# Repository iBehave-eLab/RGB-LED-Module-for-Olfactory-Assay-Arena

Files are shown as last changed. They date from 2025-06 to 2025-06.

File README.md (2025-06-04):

# RGB-LED-Module-for-Olfactory-Assay-Arena

The RGB LED Module "Model 608 revC V1.0" is specifically designed for use with the "Olfactory Assay Arena" Revision C and enables precise optogenetic control in behavioral experiments. The board supports independent control of red, green, and blue high-power LEDs across four separate channels, as well as an independently controlled IR LED. It interfaces with an Arduino Mega 2560 via serial communication, using PWM and TTL signals for intensity and status regulation. Safety features and operational constraints ensure reliable use in a laboratory setting. A comprehensive command structure allows for highly flexible integration into custom research setups. This system is not approved for human use and is intended strictly for experimental laboratory environments.

 ### Pictures

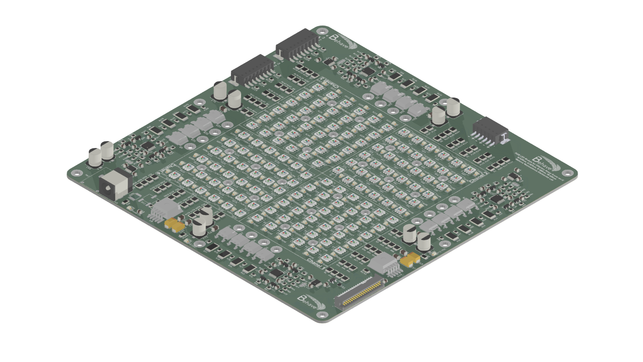
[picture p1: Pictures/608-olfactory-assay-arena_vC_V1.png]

_Rendering of the RGB-LED-Module-for-Olfactory-Assay-Arena (by Mehrdad Ghanbari)._

## Reference
The RGB-LED module "Model 608 revC V1.0" was designed as a drop-in replacement for the original single-color LED module used in the “Olfactory Assay Arena – Revision C” developed by HHMI’s Janelia Research Campus.

https://www.janelia.org/open-science/four-way-olfactometer-arena-fruit-flies
https://hhmi.flintbox.com/technologies/c65b2ddd-3cc1-44d9-a95d-73e08723f724

Our contribution is limited to adapting the original PCB layout to support three-color RGB LEDs. All mechanical components and the intended use case remain unchanged and originate entirely from the original design provided by the Janelia Research Campus.

This repository is intended solely for research and prototyping purposes. All rights to the original design and its application belong to HHMI’s Janelia Research Campus.

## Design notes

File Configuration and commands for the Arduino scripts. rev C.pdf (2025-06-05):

# RGB LED Module for Olfactory Assay Arena rev:C Model 608 revC V1.0

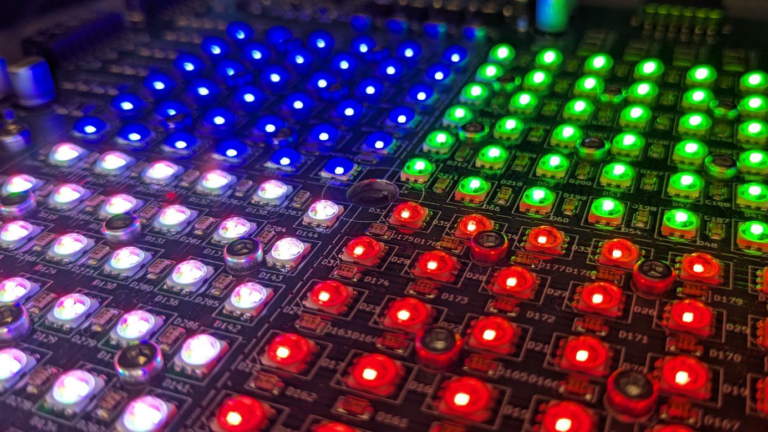
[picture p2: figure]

# OPERATOR’S MANUAL

Version A
May 2025

608 rev C V 1.0 Operator's Manual

This manual refers to the RGB LED Module for the Olfactory Assay Arena, Revision C, as currently provided (as of April 2025, version 608-C-1) by the Neuroscience Electronics Lab at the Institute of Zoology, University of Cologne.
Contacts:
- mehrdad.ghanbari@uni-koeln.de (Mehrdad Ghanbari)

The following commands are intended for use with a serial terminal. It is important to ensure that the interface baud rate is set to 115200 bits per second.
This version of the optogenetic arena uses RGB LEDs. Therefore, it is necessary to adapt the corresponding Arduino scripts to enable precise control of the LEDs. This includes modifications to the Arduino commands and configurations, as well as appropriate adjustments in serial terminal communication tools.
Important Information • The Model 608 revC V1.0 and its associated parts are not intended for experiments on

humans and must not be used for that purpose.Use on humans is strictly prohibited, unless specifically marked and insulated probes designed for such applications are used.This device is intended for laboratory use only.
- Before powering up the board, please ensure that the TTL/PWM Interface Board is properly connected to the RGB LED Module for the Olfactory Assay Arena, Revision C using the appropriate cables.This prevents the RGB LEDs from turning on unexpectedly without a command or signal.
- Do not touch the boards while they are powered on and under voltage.
- This may cause damage to components or lead to unintended malfunction. Maximum Brightness and Power Distribution The total intensity per channel must not exceed 100 %. This means:
1. You can run one LED color at 100 % while the others are off,
2. or two colors at 50 % each,
3. or three colors at approximately 35 % each.
If all three colors (Red, Green, Blue) are operated at full brightness simultaneously (3 × 100 % = 300 % on one channel), the remaining three channels must not exceed a combined total of 100 % brightness.
Thus, the total output across all four channels must not exceed 400 %.
The IR LED operates independently from the RGB LEDs and can be freely set between 0 and 100 % brightness without affecting this limitation.

# Installationshinweis

Installing the Model 608 revC V1.0 in a laboratory setting is very straightforward. It can be operated on almost any standard lab bench.
The “RGB LED Module for the Olfactory Assay Arena, Revision C” board features two power input jacks:
- Ø 2.5 mm (inner) for 24 VDC / 5 A
- Ø 2.1 mm (inner) for 9 VDC / 0.6 A

The appropriate power supplies are included.
The Arduino is powered using the included 9 VDC power supply.

Make sure the power supply matches the voltage requirements of the connected boards before plugging it in.
Do not block the ventilation side of the board to prevent overheating.

# Block Diagra

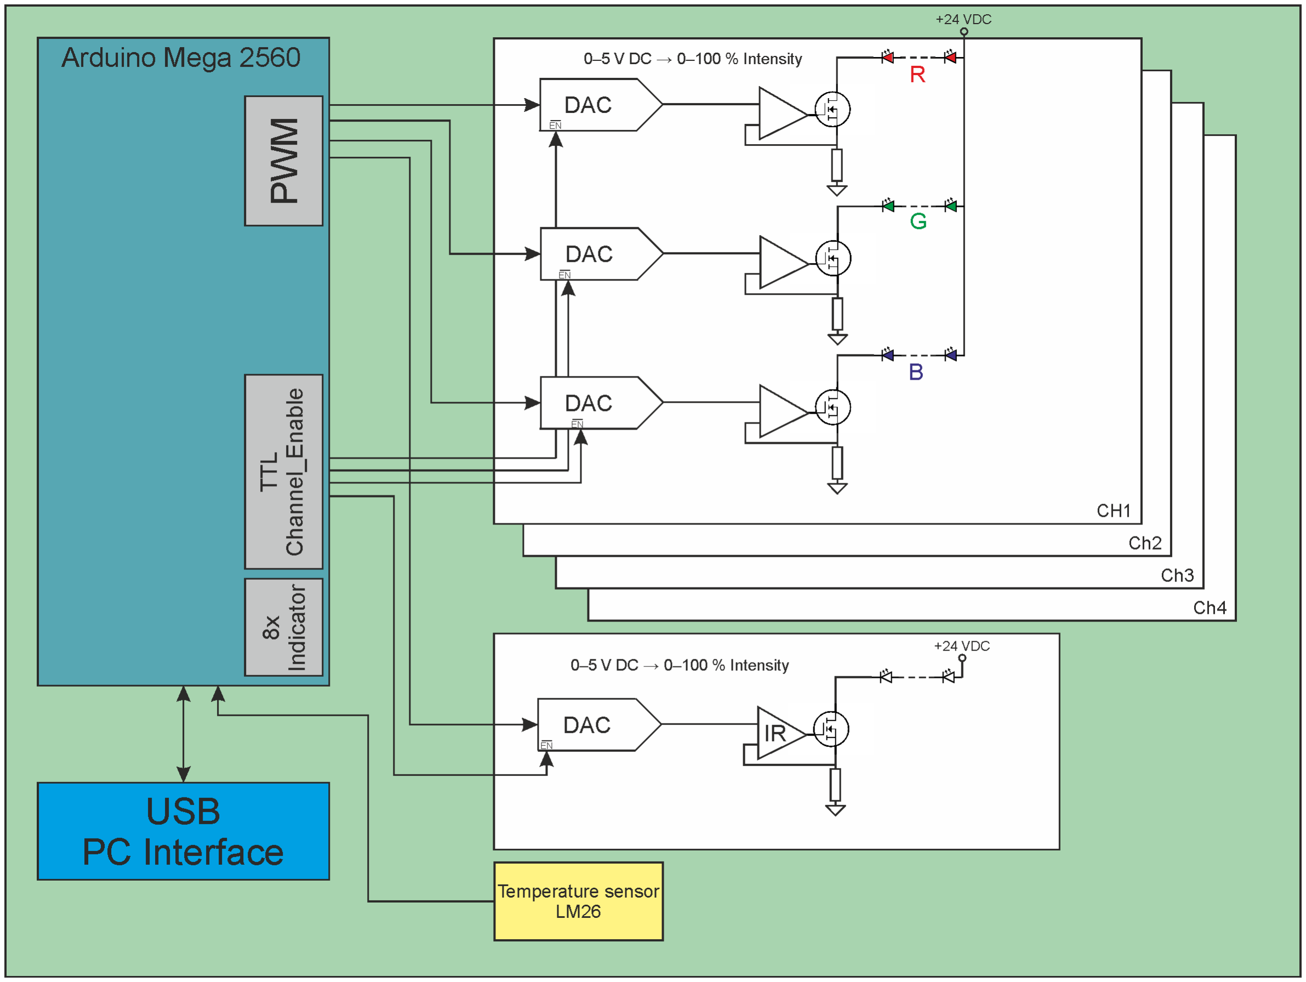
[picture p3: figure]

## The following components are included in the delivery:

1. Board 1: RGB LED Module for the Olfactory Assay Arena, Revision C
2. Board 2: TTL/PWM Interface Board
3. 2x plug-in power supplies (9 VDC, 0.66 A) – one for the Arduino, one for the 9V input of Board 1
4. Bench power supply (24 VDC, 5 A) – for the 24V input of Board 1
5. RGB PCB SUPPORT, Revision C
6. Extruded heat sink (150 × 160 × 50 mm)
7. Rectangular cable sets (for connecting the boards)
8. 4x indicator IR-LED (VSMY1850X01), 850 nm, with approx. 60 cm lead wire, with the following pin assignment:
1. Red (+) and Brown (–)
2. White (+) and Black (–)
3. Blue (+) and Green (–)
4. Violet (+) and Grey (–)

Since the new version of the arena is equipped with RGB LEDs, the new board requires multiple PWM signal outputs compared to the previous version.

For each channel, there are three PWM signals used to control the intensity of the red, green, and blue LEDs (RGB), and three TTL signals to activate or deactivate the corresponding RGB LEDs.
The IR LEDs receive one shared PWM signal and one TTL signal across all channels.

The following commands are used to control the analog and digital outputs responsible for managing the board via Arduino.
The commands are divided into three main groups.
Note: The capitalization of the commands is important and must be strictly followed.

## Control of Analog and Digital Outputs via Arduino

The following commands allow control of the analog and digital outputs of the system, specifically for the “RGB LED Module for the Olfactory Assay Arena, Revision C” via Arduino.
These functions provide flexible and precise control of light output and digital signals for a wide range of laboratory applications.

The commands are divided into five main categories:

## 1. Changing PWM Frequency for RGB and IR LEDs

The LEDs are not driven directly by the PWM signal. Instead, the PWM is filtered before reaching the LEDs, resulting in a smoothed signal that ensures stable light output.

Changing the PWM frequency is typically not necessary and has no effect on visible light behavior. However, the option exists to adjust the frequency in case interference issues arise in specific setups or environments.

- All RGB LEDs share a common frequency.
- The IR LED can be controlled with a separate frequency.

Default settings:

- RGB LEDs: 15.625 Hz
- IR LED: 7.812 Hz

Table 1: Commands for Frequency Selection of the IR LED
Mode | frequency | command
1 | 62.5 kHz | FREQ_ir_62500
2 | 7.81 kHz | FREQ_ir_7812
3 | 976 Hz | FREQ_ir_976

Table 2: Commands for Frequency Selection of the RGB LED
Mode | frequency | command
1 | 62.5 kHz | FREQ_rgb_62500
2 | 31.25 kHz | FREQ_rgb_31250
3 | 15.625 Hz | FREQ_rgb_15625
4 | 7.81 kHz | FREQ_rgb_7812
5 | 3.906 kHz | FREQ_rgb_3906
6 | 1.953 kHz | FREQ_rgb_1953
7 | 976 Hz | FREQ_rgb_976
8 | 488 Hz | FREQ_rgb_488
Example:
The following command changes the PWM frequency for the IR LED to 62,500 Hz: Sent: FREQ_ir_62500
The Arduino replies: IR LED frequency set to: 62500
For an invalid command, the Arduino replies, for example:
Sent: FREQ_rgb_6500
The Arduino replies: Ungültige RGB Frequenz

Note: Every time the frequency (for RGB or IR LED) is changed, all duty cycle values are automatically reset to 0%.
This is done to avoid errors in intensity calculation and within the Arduino script. After changing the frequency, you must redefine the duty cycle values for each LED.

As previously mentioned, changing the frequency is usually not necessary, since the PWM signal is filtered and does not affect the actual light output.

## 2. Adjusting the PWM Duty Cycle (Light Intensity)

Although the LEDs are not driven directly by the PWM signal, but by a filtered version, the duty cycle remains the key parameter for controlling light intensity.

The duty cycle defines the percentage of time the PWM signal stays HIGH during each cycle (e.g., 50%).
After filtering, this pulsed signal becomes a smoothed output voltage that is proportional to the brightness.
- A higher duty cycle results in a higher average voltage and thus brighter light.
- A lower duty cycle produces a lower average voltage and dimmer light.

This enables precise brightness control without visible flickering.

Table 3: Command for Writing an Intensity Value for an RGB LED & IR LED
command | function
PWM_red_ch1_00 … 100 | Writes a value from 0–100 (% duty cycle) to adjust the red LED of channel 1
PWM_red_ch2_00 … 100 | Writes a value from 0–100 (% duty cycle) to adjust the red LED of channel 2
PWM_red_ch3_00 … 100 | Writes a value from 0–100 (% duty cycle) to adjust the red LED of channel 3
PWM_red_ch4_00 … 100 | Writes a value from 0–100 (% duty cycle) to adjust the red LED of channel 4
PWM_green_ch1_00 … 100 | Writes a value from 0–100 (% duty cycle) to adjust the green LED of channel 1
PWM_green_ch2_00 … 100 | Writes a value from 0–100 (% duty cycle) to adjust the green LED of channel 2
PWM_green_ch3_00 … 100 | Writes a value from 0–100 (% duty cycle) to adjust the green LED of channel 3
PWM_green_ch4_00 … 100 | Writes a value from 0–100 (% duty cycle) to adjust the green LED of channel 4
PWM_blue_ch1_00 … 100 | Writes a value from 0–100 (% duty cycle) to adjust the blue LED of channel 1
PWM_ blue_ch2_00 … 100 | Writes a value from 0–100 (% duty cycle) to adjust the blue LED of channel 2
PWM_ blue_ch3_00 … 100 | Writes a value from 0–100 (% duty cycle) to adjust the blue LED of channel 3
PWM_ blue_ch4_00 … 100 | Writes a value from 0–100 (% duty cycle) to adjust the blue LED of channel 4
PWM_ ir_led_00 … 100 | Writes a value from 0–100 (% duty cycle) to adjust the IR LED

Example:
Sent: PWM_red_ch3_37
→ Sets the red LED of channel 3 to 75% intensity.

## 3. Activating/Deactivating Individual LEDs

- Each red, green, and blue LED per channel can be controlled individually (on/off).
- IR LEDs are switched collectively for all channels.

The third command group is used to enable or disable the RGB LEDs and the IR LED.
With the corresponding commands, individual RGB LEDs and the IR LED can be turned on or off. When enabled, the LED operates using the previously set PWM value.

Table 4: command to enable or disable the RGB LEDs and the IR LED
command | function
EN_red_ch1_1 | Enable LED red Chanel 1
EN_red_ch1_0 | Disable LED red Chanel 1
EN_red_ch1_1 | Enable LED red Chanel 2
EN_red_ch1_0 | Disable LED red Chanel 2
EN_red_ch1_1 | Enable LED red Chanel 3
EN_red_ch1_0 | Disable LED red Chanel 3
EN_red_ch1_1 | Enable LED red Chanel 4
EN_red_ch1_0 | Disable LED red Chanel 4
EN_ green _ch1_1 | Enable LED green Chanel 1
EN_ green _ch1_0 | Disable LED green Chanel 1
EN_ green _ch1_1 | Enable LED green Chanel 2
EN_ green _ch1_0 | Disable LED green Chanel 2
EN_ green _ch1_1 | Enable LED green Chanel 3
EN_ green _ch1_0 | Disable LED green Chanel 3
EN_ green _ch1_1 | Enable LED green Chanel 4
EN_ green _ch1_0 | Disable LED green Chanel 4
EN_blue_ch1_1 | Enable LED blue Chanel 1
EN_ blue _ch1_0 | Disable LED blue Chanel 1
EN_ blue _ch1_1 | Enable LED blue Chanel 2
EN_ blue _ch1_0 | Disable LED blue Chanel 2
EN_ blue _ch1_1 | Enable LED blue Chanel 3
EN_ blue _ch1_0 | Disable LED blue Chanel 3
EN_ blue _ch1_1 | Enable LED blue Chanel 4
EN_ blue _ch1_0 | Disable LED blue Chanel 4
EN_ir_led_1 | Enable LED red Chanel IR
EN_ir_led_2 | Disable LED red Chanel IR

## 4. Control of the 8 Digital Outputs

The board features a total of eight digital outputs that can be used flexibly as status indicators, control lines, or trigger signals.

- The outputs are divided into two groups: Group A and Group B, each containing four outputs.
- Each output can be individually set to HIGH or LOW.
- The outputs are visible directly on the board and can be controlled via software.
- Although labeled as “indicators” on the board, they can be used for various other purposes as well.

This setup simplifies seamless integration of the board with other devices and systems in the laboratory environment.

The fourth command group is used to activate or deactivate the eight digital outputs.

Using the corresponding commands, each individual digital output can be selectively switched on or off.

Table 5: command to enable or disable Digital Outputs
command | function
IND_1_1 | Enable indicator 1 (Ind A-1)
IND_1_0 | Disable indicator 1 (Ind A-1)
IND_2_1 | Enable indicator 2 (Ind B-1)
IND_2_0 | Disable indicator 2 (Ind B-1)
IND_3_1 | Enable indicator 3 (Ind A-2)
IND_3_0 | Disable indicator 3 (Ind A-2)
IND_4_1 | Enable indicator 4 (Ind B-2)
IND_4_0 | Disable indicator 4 (Ind B-2)
IND_5_1 | Enable indicator 5 (Ind A-3)
IND_5_0 | Disable indicator 5 (Ind A-3)
IND_6_1 | Enable indicator 6 (Ind B-3)
IND_6_0 | Disable indicator 6 (Ind B-3)
IND_7_1 | Enable indicator 7 (Ind A-4)
IND_7_0 | Disable indicator 7 (Ind A-4)
IND_8_1 | Enable indicator 8 (Ind B-4)
IND_8_0 | Disable indicator 8 (Ind B-4)

## 5. Reading the board temperature:

The built-in temperature sensor is connected to analog pin A0 on the Arduino. You can read the current board temperature using the following command:
Sent: TEMP
When this command is sent to the Arduino via the serial port, the Arduino responds with the current temperature in degrees Celsius.
Note:
The temperature sensor has no other function besides measuring temperature. However, the measured value can be used in the software – for example, to automatically turn off the LED at a certain temperature. This helps reduce the risk of damaging the board due to overheating.

## PWM Outputs and Control Signals of the Arduino Mega 2560

for Multi-Channel LED Driver Systems The following list outlines the pin configuration of the Arduino Mega 2560 used in a multi-channel

LED and infrared control system. Various PWM-capable pins are assigned to drive infrared LEDs and RGB LED channels. Additional pins are designated to enable individual color channels. Furthermore, several digital outputs are reserved for controlling four indicator units (IND_1A to IND_4B). Each pin’s function, including its PWM capability and associated port, is listed in detail below.

Table 6: Pinout Arduino to Board
Pin Arduino | Pin Register | Timmer | Function
4 | PG5 | OC0B | ir_led
13 | PB7 | OC1C | red_ch1
12 | PB6 | OC1B | green_ch1
11 | PB5 | OC1A | blue_ch1
3 | PE5 | OC3C | red_ch2
2 | PE4 | OC3B | green_ch2
5 | PE3 | OC3A | blue_ch2
8 | PH5 | OC4C | red_ch3
7 | PH4 | OC4B | green_ch3
6 | PH3 | OC4A | blue_ch3
44 | PL5 | OC5C | red_ch4
45 | PL4 | OC5B | green_ch4
46 | PL3 | OC5A | blue_ch4
30 | PC7 | | Enable red_ch1
31 | PC6 | | Enable green_ch1
32 | PC5 | | Enable blue_ch1
33 | PC4 | | Enable red_ch2
34 | PC3 | | Enable green_ch2
35 | PC2 | | Enable blue_ch2
36 | PC1 | | Enable red_ch3
37 | PC0 | | Enable green_ch3

38 | PD7 | Enable blue_ch3
39 | PG2 | Enable red_ch4
40 | PG1 | Enable green_ch4
41 | PG0 | Enable blue_ch4
42 | PL7 | Enable IR_LED
22 | PA0 | IND_1A
23 | PA1 | IND_1B
24 | PA2 | IND_2A
25 | PA3 | IND_2B
26 | PA4 | IND_3A
27 | PA5 | IND_3B
28 | PA6 | IND_4A
29 | PA7 | IND_4B
A0 | | Temperature sensor

## Explanation of the Measurement

The LED intensity was measured using a photodiode detector of type PH100-Si, which features a 10 mm aperture. The detector was positioned on a flat surface (measurement arena) at a fixed distance of 10 cm from the LED, ensuring consistent optical coupling. The power calibration of the sensor has an uncertainty of approximately ±2%.

The measurement was performed with the board in a cold state, i.e., before any significant self-heating due to prolonged operation occurred. It should be noted that rising temperatures can affect the measured values, as LED output is temperature-dependent.

Table 7: LED Intensity vs. Duty Cycle
| Light Intensity (mW)
Duty Cycle (%) | Red 625nm | Green 525nm | Blue 460nm | IR 850nm
0 | 0 | 0 | 0 | 0
6 | 0,15 | 0,174 | 0,266 | 0,217
10 | 0,78 | 0,67 | 1,12 | 0,68
20 | 2,27 | 1,85 | 3,3 | 1,92
30 | 3,73 | 2,83 | 5,31 | 3,12
40 | 5,24 | 3,75 | 7,33 | 4,34
50 | 6,66 | 4,54 | 9,19 | 5,49
60 | 8,14 | 5,32 | 11,1 | 6,68
70 | 9,53 | 6 | 12,8 | 7,8
80 | 11 | 6,68 | 14,6 | 8,93
90 | 12,4 | 7,31 | 16,3 | 10,1
100 | 13,6 | 7,88 | 17,9 | 10,9

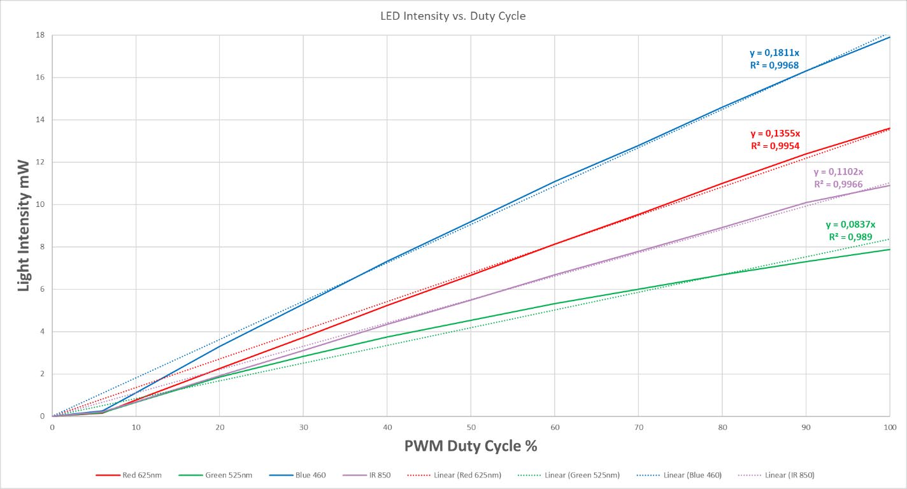
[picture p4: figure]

In addition to intensity measurements, the emitted wavelengths of the LEDs were also checked. The measured wavelengths showed slight deviations from the nominal values provided by the manufacturer, as shown in the following table:

LED | Nominal Wavelength | Measured Wavelength
Red | 625 nm | 630 nm
Green | 525 nm | 527 nm
Blue | 460 nm | 458 nm
IR | 850 nm | 858 nm

These deviations can result from manufacturing tolerances in the LEDs as well as the spectral response characteristics of the detector.

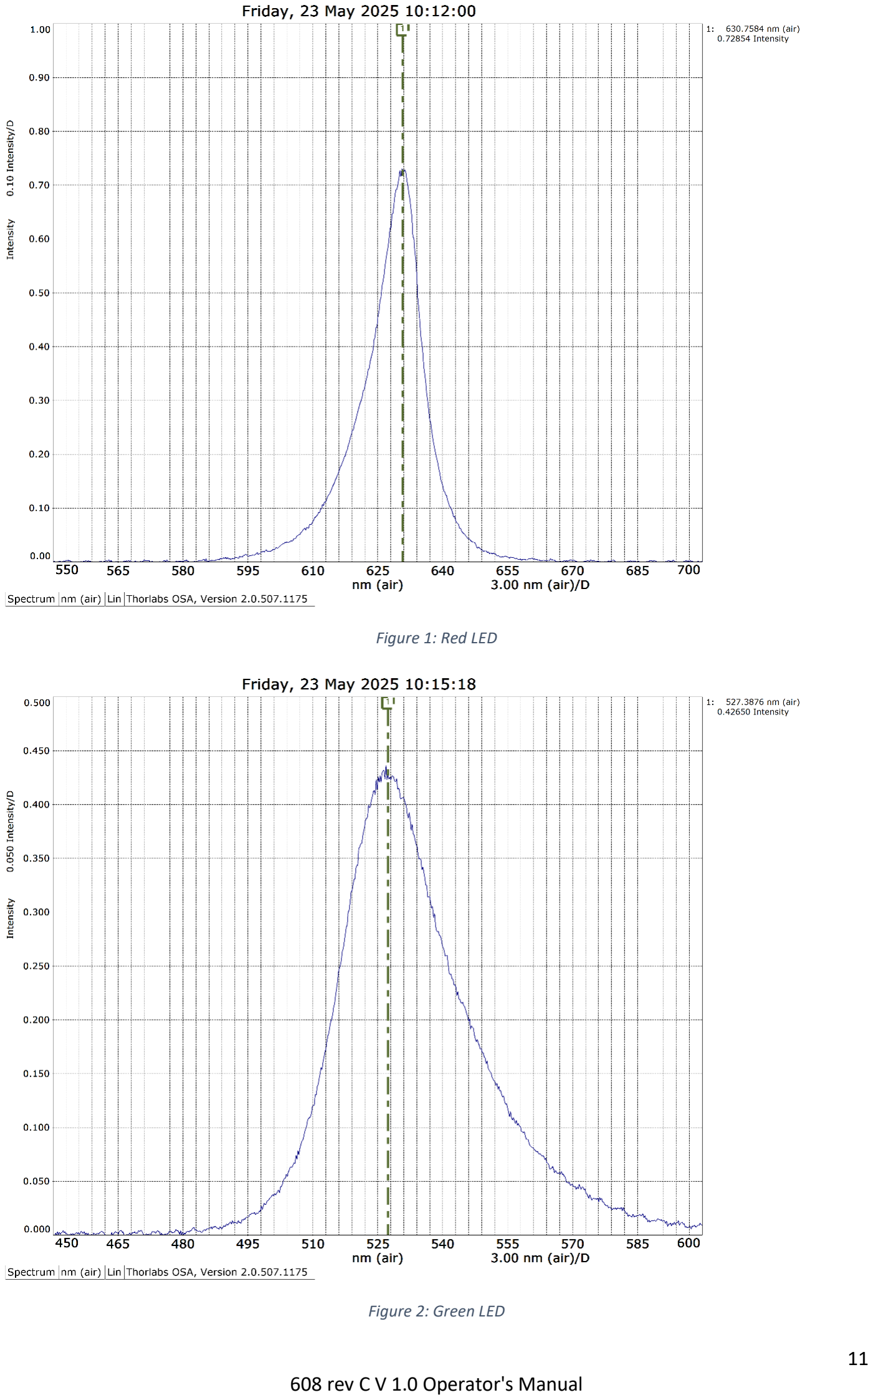
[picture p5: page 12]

Figure 1: Red LED

Figure 2: Green LED

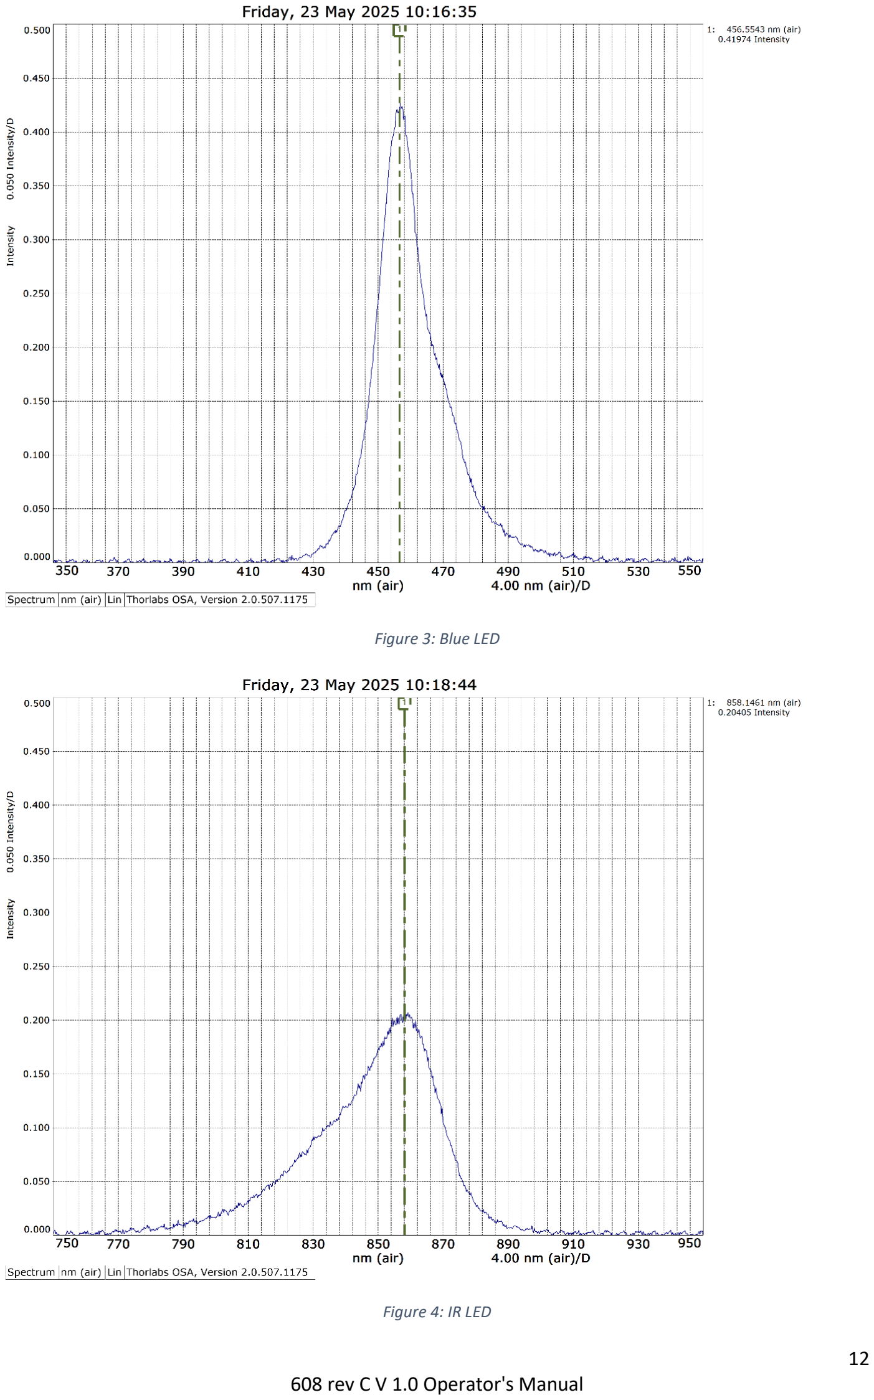
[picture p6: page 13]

Figure 3: Blue LED

Figure 4: IR LED

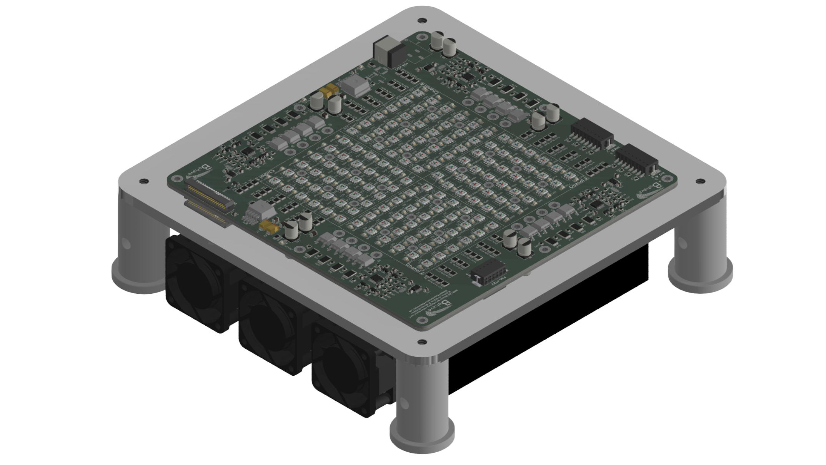
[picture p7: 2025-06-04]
Pictures/608-olfactory-assay-rev C.png

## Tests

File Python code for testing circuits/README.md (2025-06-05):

To test the board, a graphical user interface (GUI) developed in Python is provided. The GUI sends serial commands to an Arduino Mega, which is responsible for controlling the board. This setup allows for easy verification and control of various functions and processes on the board. The combination of the Python GUI and Arduino creates a simple and efficient testing environment.

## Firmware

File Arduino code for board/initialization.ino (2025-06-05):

void initialize_pin() {
  // Pins 22-41 als Ausgänge definieren
  // Port A (Pins 22-29)
  DDRA = 0xFF;  // Alle Pins von Port A als Ausgang

  // Port C (Pins 30-37)
  DDRC = 0xFF;  // Alle Pins von Port C als Ausgang

  // Port D (Pin 38)
  DDRD = _BV(DDD7);  // Pin 38 als Ausgang

  // Port G (Pins 39-41)
  DDRG = _BV(DDG2) | _BV(DDG1) | _BV(DDG0);  // Pins 39, 40, 41 als Ausgang

  DDRL |= (1 << PL7);  // Setzt Pin 42 als Ausgang

  // PWM-Pins konfigurieren
  // Port B (Pins 11, 12, 13 für PWM)
  DDRB |= _BV(DDB7) | _BV(DDB6) | _BV(DDB5);  // OC1C, OC1B, OC1A (Pins 13, 12, 11)

  // Port E (Pins 2, 3, 5 für PWM)
  DDRE |= _BV(DDE5) | _BV(DDE4) | _BV(DDE3);  // OC3C, OC3B, OC3A (Pins 3, 2, 5)

  // Port H (Pins 6, 7, 8 für PWM)
  DDRH |= _BV(DDH5) | _BV(DDH4) | _BV(DDH3);  // OC4C, OC4B, OC4A (Pins 8, 7, 6)

  // Port L (Pins 44, 45, 46 für PWM)
  DDRL |= _BV(DDL5) | _BV(DDL4) | _BV(DDL3);  // OC5C, OC5B, OC5A (Pins 44, 45, 46)

  // Port G (Pin 4 für PWM)
  DDRG |= _BV(DDG5);  // OC0B (Pin 4)

  // Alle Ausgänge auf LOW setzen
  PORTA = 0;
  PORTC = 0xFF;                                // Alle Ausgänge 30-37 auf HOGH setzen
  PORTD |= _BV(PD7);                           // Nur Pin 38 auf HIGH setzen, andere nicht ändern
  PORTG |= _BV(PG2) | _BV(PG1) | _BV(PG0);     // Pins 39, 40, 41 auf HIGH setzen
  PORTL |= _BV(PL7);                           // Setzt Pin 42 auf HIGH
  PORTG &= ~_BV(PG5);                          // Pin 4 separat auf LOW setzen
  PORTB &= ~(_BV(PB7) | _BV(PB6) | _BV(PB5));  // Pins 13, 12, 11 auf LOW setzen
  PORTE &= ~(_BV(PE5) | _BV(PE4) | _BV(PE3));  // Pins 3, 2, 5 auf LOW setzen
  PORTH &= ~(_BV(PH5) | _BV(PH4) | _BV(PH3));  // Pins 8, 7, 6 auf LOW setzen
  PORTL &= ~(_BV(PL5) | _BV(PL4) | _BV(PL3));  // Pins 44, 45, 46 auf LOW setzen


  // Timer 0 konfigurieren (8-bit) - für ir_led (Pin 4)
  TCCR0A = _BV(COM0B1) | _BV(WGM01) | _BV(WGM00);  // Fast PWM 8bit, nicht-invertierend
  TCCR0B = _BV(CS01);                              // Kein Prescaler
  OCR0B = 0;                                       // PWM auf 0% setzen



  // Timer 1 konfigurieren (8-bit) - für RGB ch1 (Pins 11, 12, 13)
  TCCR1A = _BV(COM1A1) | _BV(COM1B1) | _BV(COM1C1)| _BV(WGM11) | _BV(WGM10);  // Fast PWM 10-bit, nicht-invertierend
  TCCR1B = _BV(WGM12) | _BV(CS10);                                // Fast PWM, kein Prescaler
  OCR1A = 0;                                                      // Blue Ch1 PWM auf 0%
  OCR1B = 0;                                                      // Green Ch1 PWM auf 0%
  OCR1C = 0;                                                      // Red Ch1 PWM auf 0%

  // Timer 3 konfigurieren (8-bit) - für RGB ch2 (Pins 2, 3, 5)
  TCCR3A = _BV(COM3A1) | _BV(COM3B1) | _BV(COM3C1)| _BV(WGM31) | _BV(WGM30);  // Fast PWM 10-bit, nicht-invertierend
  TCCR3B = _BV(WGM32) | _BV(CS30);                                // Fast PWM, kein Prescaler
  OCR3A = 0;                                                      // Blue Ch2 PWM auf 0%
  OCR3B = 0;                                                      // Green Ch2 PWM auf 0%
  OCR3C = 0;                                                      // Red Ch2 PWM auf 0%

  // Timer 4 konfigurieren (8-bit) - für RGB ch3 (Pins 6, 7, 8)
  TCCR4A = _BV(COM4A1) | _BV(COM4B1) | _BV(COM4C1)| _BV(WGM41) | _BV(WGM40);  // Fast PWM 10-bit, nicht-invertierend
  TCCR4B = _BV(WGM42) | _BV(CS40);                                // Fast PWM, kein Prescaler
  OCR4A = 0;                                                      // Blue Ch3 PWM auf 0%
  OCR4B = 0;                                                      // Green Ch3 PWM auf 0%
  OCR4C = 0;                                                      // Red Ch3 PWM auf 0%

  // Timer 5 konfigurieren (8-bit) - für RGB ch4 (Pins 44, 45, 46)
  TCCR5A = _BV(COM5A1) | _BV(COM5B1) | _BV(COM5C1)| _BV(WGM51) | _BV(WGM50);  // Fast PWM 10-bit, nicht-invertierend
  TCCR5B = _BV(WGM52) | _BV(CS50);                                // Fast PWM, kein Prescaler
  OCR5A = 0;                                                      // Blue Ch4 PWM auf 0%
  OCR5B = 0;                                                      // Green Ch4 PWM auf 0%
  OCR5C = 0;                                                      // Red Ch4 PWM auf 0%
}

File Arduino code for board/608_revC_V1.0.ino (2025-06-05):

/*
pin # 4(OC0B)(PG5)pwm signal      to ir_led
pin # 13(OC1C)(PB7)pwm signal     to red_ch1
pin # 12(OC1B)(PB6)pwm signal     to green_ch1
pin # 11(OC1A)(PB5)pwm signal     to blue_ch1
pin # 3(OC3C)(PE5)pwm signal      to red_ch2
pin # 2(OC3B)(PE4)pwm signal      to green_ch2
pin # 5(OC3A)(PE3)pwm signal      to blue_ch2
pin # 8(OC4C)(PH5)pwm signal      to red_ch3
pin # 7(OC4B)(PH4)pwm signal      to green_ch3
pin # 6(OC4A)(PH3)pwm signal      to blue_ch3
pin # 44(OC5C)(PL5)pwm signal     to red_ch4
pin # 45(OC5B)(PL4)pwm signal     to green_ch4
pin # 46(OC5A)(PL3)pwm signal     to blue_ch4
pin # 30  to Enable red_ch1       PORTC7
pin # 31  to Enable green_ch1     PORTC6
pin # 32  to Enable blue_ch1      PORTC5
pin # 33  to Enable red_ch2       PORTC4
pin # 34  to Enable green_ch2     PORTC3
pin # 35  to Enable blue_ch2      PORTC2
pin # 36  to Enable red_ch3       PORTC1
pin # 37  to Enable green_ch3     PORTC0
pin # 38  to Enable blue_ch3      PORTD7
pin # 39  to Enable red_ch4       PORTG2
pin # 40  to Enable green_ch4     PORTG1
pin # 41  to Enable blue_ch4      PORTG0
pin # 42  to Enable ir_led        PORTL7
pin # 22 to IND_1A
pin # 23 to IND_1B
pin # 24 to IND_2A
pin # 25 to IND_2B
pin # 26 to IND_3A
pin # 27 to IND_3B
pin # 28 to IND_4A
pin # 29 to IND_4B
*/

// Variable zum Speichern der eingehenden seriellen Daten als Zeichenkette
String serial_info;
const unsigned long frequencies[] = { 62500, 31250, 15625, 7812, 3906, 1953, 976, 488 };
const unsigned long ir_frequencies[] = { 62500, 7812, 976 };

// 2D-Array zur Speicherung der Duty-Werte für die 12 möglichen Kombinationen von Farben und Kanälen
// Farben: 0 = Rot, 1 = Grün, 2 = Blau
// Kanäle: 0 bis 3
int dutyValues[3][4] = { 0 };  // Initialisierung aller Werte mit 0
// 2D-Array zur Speicherung der EN für die 12 möglichen Kombinationen von Farben und Kanälen
// Farben: 0 = Rot, 1 = Grün, 2 = Blau
// Kanäle: 0 bis 3
int rgbPinEN[3][4] = { 0 };  // Initialisierung aller Werte mit 0
// Variable zur Speicherung des Duty-Werts für den IR-Kanal
int ir_dutyValues = 0;  // Initialisiert mit 0
// Variable zur Speicherung des EN für den IR-Kanal
int irPinEN = 0;  // Initialisiert mit 0

uint16_t old_OCR0B = 0;
uint16_t old_OCR1A = 0;
uint16_t old_OCR1B = 0;
uint16_t old_OCR1C = 0;
uint16_t old_OCR3A = 0;
uint16_t old_OCR3B = 0;
uint16_t old_OCR3C = 0;
uint16_t old_OCR4A = 0;
uint16_t old_OCR4B = 0;
uint16_t old_OCR4C = 0;
uint16_t old_OCR5A = 0;
uint16_t old_OCR5B = 0;
uint16_t old_OCR5C = 0;

int Indikator[8] = { 0 };
int sensorValue = analogRead(A0);

// Setup-Funktion wird einmal beim Start des Mikrocontrollers ausgeführt
void setup() {
  initialize_pin();      // Initialisiert die Pins
  Serial.begin(115200);  // Initialisiert die serielle Kommunikation mit 115200 Baud
}

// Hauptprogramm (Loop-Funktion), das kontinuierlich wiederholt wird
void loop() {
  // Prüft, ob serielle Daten verfügbar sind
  if (Serial.available() > 0) {
    // Liest die ankommende Zeichenkette bis zum Zeilenumbruch ('\n')
    serial_info = Serial.readStringUntil('\n');

    // Gibt die empfangene Zeichenkette zur Überprüfung auf der seriellen Konsole aus
    //Serial.println(serial_info);

    // Leert den seriellen Puffer (nicht unbedingt notwendig)
    Serial.flush();

    // Ruft die Funktion zur Verarbeitung der empfangenen Parameter auf
    getParam();
  }
}

// Funktion zur Extraktion und Verarbeitung der Parameter aus dem seriellen Befehl
int getParam() {
  // Prüft, ob die empfangene Nachricht mit "PWM" beginnt
  if (serial_info.startsWith("PWM")) {
    // Findet die Positionen der Trennzeichen ('_') in der Nachricht
    int spaceIndex1 = serial_info.indexOf('_');                   // Erstes '_'
    int spaceIndex2 = serial_info.indexOf('_', spaceIndex1 + 1);  // Zweites '_'
    int spaceIndex3 = serial_info.indexOf('_', spaceIndex2 + 1);  // Drittes '_'

    // Überprüft, ob alle Trennzeichen vorhanden sind
    if (spaceIndex1 != -1 && spaceIndex2 != -1 && spaceIndex3 != -1) {
      // Extrahiert die Farb-, Kanal- und Duty-Zeichenketten aus der Nachricht
      String colorStr = serial_info.substring(spaceIndex1 + 1, spaceIndex2);
      String channelStr = serial_info.substring(spaceIndex2 + 1, spaceIndex3);
      String dutyStr = serial_info.substring(spaceIndex3 + 1);

      // Konvertiert den Duty-Wert in eine Ganzzahl
      int dutyCycle = dutyStr.toInt();

      // Übergibt die extrahierten Werte an die Funktion zur Aktualisierung des Arrays
      updateDutyValue(colorStr, channelStr, dutyCycle);
    }
  }
  // Für IR-LED Frequenz
  if (serial_info.startsWith("FREQ_ir_")) {
    String freq_str = serial_info.substring(8);  // Extrahiere den Frequenzwert nach "FREQ_ir_"
    unsigned long freq = freq_str.toInt();       // Konvertiere String zu Integer

    // Überprüfen, ob die Frequenz in der Liste enthalten ist
    for (int i = 0; i < 3; i++) {
      if (freq == ir_frequencies[i]) {
        set_ir_frequency(freq);
        Serial.print("IR LED Frequenz gesetzt auf: ");
        Serial.println(freq);
        return;
      }
    }

    // Wenn keine passende Frequenz gefunden wurde
    Serial.println("Ungültige IR Frequenz");
  }

  // Für RGB-LED Frequenz
  else if (serial_info.startsWith("FREQ_rgb_")) {
    String freq_str = serial_info.substring(9);  // Extrahiere den Frequenzwert nach "FREQ_rgb_"
    unsigned long freq = freq_str.toInt();       // Konvertiere String zu Integer

    // Überprüfen, ob die Frequenz in der Liste enthalten ist
    for (int i = 0; i < 8; i++) {
      if (freq == frequencies[i]) {
        set_rgb_frequency(freq);
        Serial.print("RGB LED Frequenz gesetzt auf: ");
        Serial.println(freq);
        return;
      }
    }

    // Wenn keine passende Frequenz gefunden wurde
    Serial.println("Ungültige RGB Frequenz");
  }

  if (serial_info.startsWith("EN")) {
    // Findet die Positionen der Trennzeichen ('_') in der Nachricht
    int spaceIndex1 = serial_info.indexOf('_');                   // Erstes '_'
    int spaceIndex2 = serial_info.indexOf('_', spaceIndex1 + 1);  // Zweites '_'
    int spaceIndex3 = serial_info.indexOf('_', spaceIndex2 + 1);  // Drittes '_'

    // Überprüft, ob alle Trennzeichen vorhanden sind
    if (spaceIndex1 != -1 && spaceIndex2 != -1 && spaceIndex3 != -1) {
      // Extrahiert die Farb-, Kanal- und Pinmode
      String colorStr = serial_info.substring(spaceIndex1 + 1, spaceIndex2);
      String channelStr = serial_info.substring(spaceIndex2 + 1, spaceIndex3);
      String pinModeStr = serial_info.substring(spaceIndex3 + 1);

      // Konvertiert pinModeStr in eine Ganzzahl
      int pinMode = pinModeStr.toInt();

      // Übergibt die extrahierten Werte an die Funktion zur Aktualisierung des Arrays
      updatePinMode(colorStr, channelStr, pinMode);
    }
  }
  if (serial_info.startsWith("IND")) {
    // Findet die Positionen der Trennzeichen ('_') in der Nachricht
    int spaceIndex1 = serial_info.indexOf('_');                   // Erstes '_'
    int spaceIndex2 = serial_info.indexOf('_', spaceIndex1 + 1);  // Zweites '_'
    // Überprüft, ob alle Trennzeichen vorhanden sind
    if (spaceIndex1 != -1 && spaceIndex2 != -1) {
      String indStr = serial_info.substring(spaceIndex1 + 1, spaceIndex2);
      String enStr = serial_info.substring(spaceIndex2 + 1);

      int indPin = indStr.toInt();
      int ENMode = enStr.toInt();
      if (indPin >= 1 && indPin <= 8 && (ENMode == 0 || ENMode == 1)) {
        Indikator[indPin - 1] = ENMode;
        //Serial.print("Gespeichert: IND_");
        //Serial.print(indPin);
        //Serial.print("_");
        //Serial.println(ENMode);
        if (ENMode == 1) {
          PORTA |= (1 << indPin - 1);  // Setzt das entsprechende Bit auf HIGH
        } else {
          PORTA &= ~(1 << indPin - 1);  // Setzt das entsprechende Bit auf LOW
        }
      } else Serial.println("Fehler: Ungültige Aktivität des Indikators");
    }
  }
  if (serial_info.startsWith("TEMP")) {
    float sensorValue_bit = analogRead(A0);
    sensorValue_bit = sensorValue_bit * 5 / 1024;
    float Temperatur = (-1525.04) + sqrt(2.4182e6 + ((1.8015 - sensorValue_bit) / (3.479e-6)));
    Serial.println(Temperatur,2);
  }
}

// Funktion zur Aktualisierung der Duty-Werte basierend auf Farbe und Kanal
void updateDutyValue(String color, String channel, unsigned int duty) {
  int colorIndex = -1;    // Initialisierung des Farbindex
  int channelIndex = -1;  // Initialisierung des Kanalindex

  // Wandelt die Farbzeichenkette in den entsprechenden Index um
  if (color == "red") colorIndex = 0;
  else if (color == "green") colorIndex = 1;
  else if (color == "blue") colorIndex = 2;
  else if (color == "ir") colorIndex = 3;

  // Wandelt die Kanalzeichenkette in den entsprechenden Index um (1-4 → 0-3)
  if (channel == "ch1") channelIndex = 0;
  else if (channel == "ch2") channelIndex = 1;
  else if (channel == "ch3") channelIndex = 2;
  else if (channel == "ch4") channelIndex = 3;
  else if (channel == "led") channelIndex = 4;

  // Überprüft, ob die Eingaben gültig sind
  if (colorIndex != -1 && channelIndex >= 0 && channelIndex < 4) {
    // Speichert den neuen Duty-Wert im Array
    dutyValues[colorIndex][channelIndex] = duty;

    // Gibt eine Bestätigung der Speicherung über die serielle Schnittstelle aus
    //Serial.print("Gespeichert: Duty_");
    //Serial.print(color);
    //Serial.print("_");
    //Serial.print(channel);
    //Serial.print(" = ");
    //Serial.println(duty);
  }
  // Falls es sich um den Infrarot-Kanal (ir) und den LED-Kanal handelt
  else if (colorIndex == 3 && channelIndex == 4) {
    ir_dutyValues = duty;  // Speichert den Wert in der IR-Variable

    // Gibt eine Bestätigung der Speicherung über die serielle Schnittstelle aus
    //Serial.print("Gespeichert: Duty_");
    //Serial.print(color);
    //Serial.print("_");
    //Serial.print(channel);
    //Serial.print(" = ");
    //Serial.println(duty);
  }
  // Falls eine ungültige Eingabe gemacht wurde
  else {
    Serial.println("Fehler: Ungültige Farbe oder Kanal.");
  }
  updatePWMForChannelAndColor(colorIndex, channelIndex, duty);
}
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
